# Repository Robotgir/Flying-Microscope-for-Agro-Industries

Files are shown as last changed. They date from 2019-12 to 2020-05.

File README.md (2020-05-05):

# Flying Microscope (SPECTORS)
This repo contains hardware and software details for the spore collector device which can be remotely controlled via Spectors Cockpit. Live image can be acessed on Spectors Cockpit.
## Code 
contains main script file named sporecollector1.py and its dependensies
### noteson_code.docx 
few details about the input variables in sporecollector1.py

## Docs 
contais system chart hand sketch  (Digital version yet to come)
### SystemChart.png coming soon
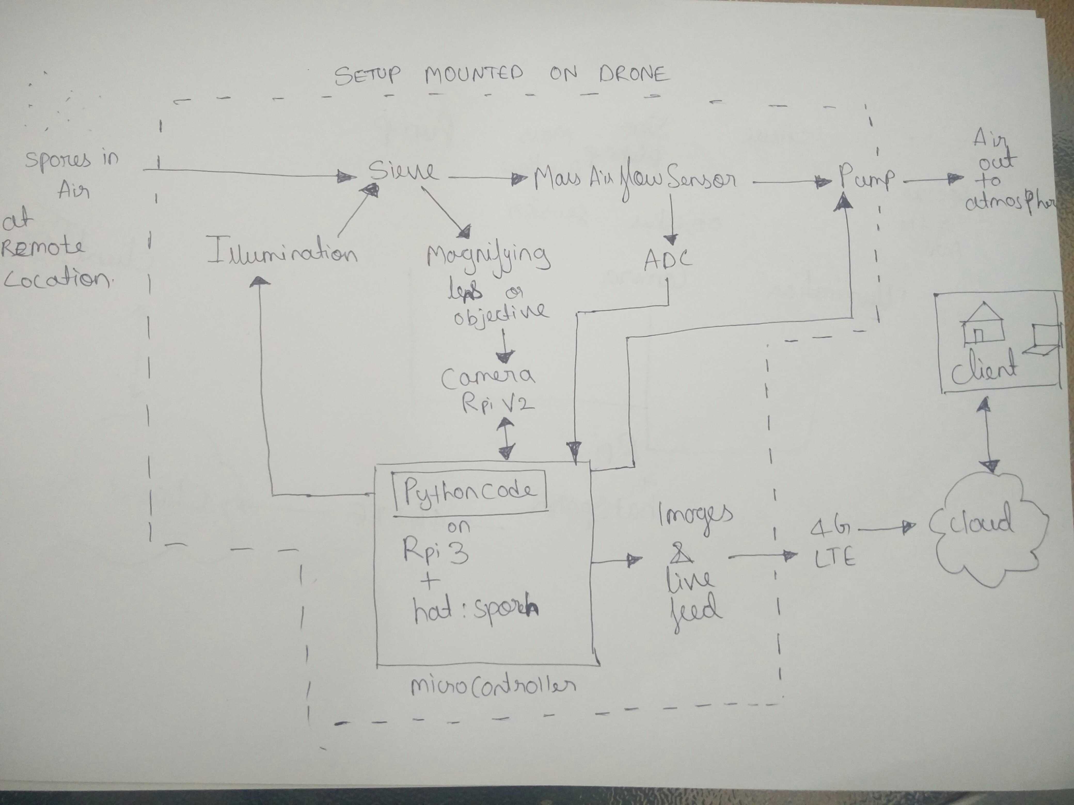
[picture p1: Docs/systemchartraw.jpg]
//

## Hardware
### camera_sieveholderassembly
contains priliminary and current designs for the spore collector device
### PCB (RPI HAT)
 contains Eagle board and schematic files for the PCB design
### productdata sheets
contain all the hardware components datasheets
#### PCB_connection_notes.docx 
contains details of how to setup the PCB AS Rpi-hat, connections with other components.

## Spore collection images
Images obtained from the measurment process
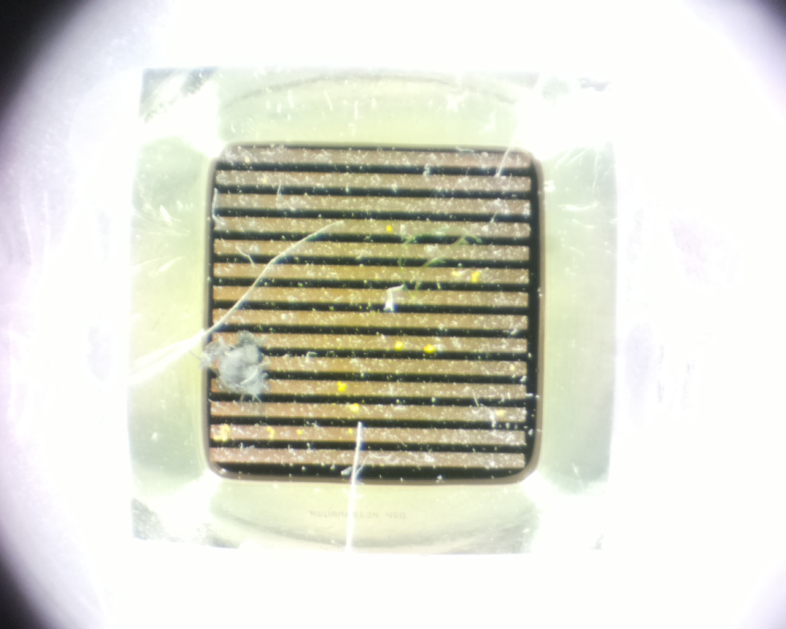
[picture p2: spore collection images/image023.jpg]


## PCB-Rpi-hat
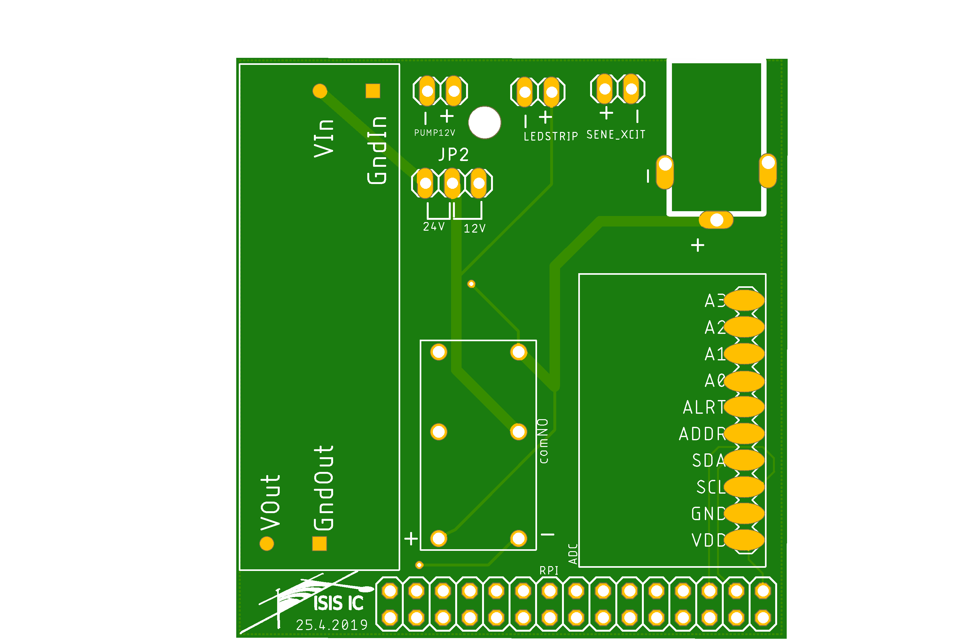
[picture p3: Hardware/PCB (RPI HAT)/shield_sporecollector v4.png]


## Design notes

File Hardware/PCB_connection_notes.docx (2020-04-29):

Two options available to choose:
The design of Rpi hat for spore collection device can be integrated with either 24V or 12V pump.
On board voltage step up regulator steps up the fixed input 12V to 24V (can be used when 24V pump is used in the spore collector device).

Steps to connect Rpi hat follow:

1. Use a jumper connector to connect the pin pair either 24V or 12V (Red circle) pair depending on the rated - pump voltage installed in the device.
2. If using a 12V pump, connect the power supply cables of pump to the 12V + - pins on the Rpi hat (blue circle).
3. If using 24V pump, connect the power supply cables of pump to the Vout and Gndout pins (yellow circle )on the Rpi-hat.
4. Power supply cables of the Led-strip to the pins in purple circle.
5. Sensor power supply cables to the respective pins as indicated on the Rpi-hat.
Note:
If the jumper pin is connected wrongly then the pump will not be supplied power as it can be seen the outlets for 12V and 24V are different.
Warning!!|


If pumps are not connected in respect to their designated pins based on their rated voltage malfunctioning of the pump and the Rpi is inevitable.

Powering the Rpi-hat:
Supply 12 V with min 3 amp

Powering the Rpi:

The Rpi, itself has to be powered separately with 5V 2.5 amp.

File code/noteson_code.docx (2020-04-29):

Location on the Rpi sd card:
cd Documents/sporecollector/Sporecollector1.py

Notes on the code, for the spore collection process:

Amount of liters to be sucked can be changed by assigning desired amount of liters to be sucked to the variable z of function measurmentprocess() in “sporecollector1.py”

Variable “i” of function ledcam() in “sporecollector1.py”sets the number of pictures to be taken during the measurement process

Interval at which the pictures are to be taken can be set by changing the j in time.sleep(j).
where, j is in seconds.

To stop the measurement process:
Hit ctrl+c

Location of the captured images:
"/home/pi/Documents/sporecollector/trailcam"

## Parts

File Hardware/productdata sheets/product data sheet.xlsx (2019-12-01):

PRODUCT | COMPANY NAME | MODEL NUMBER | SPECIFICATION | VOLTAGE [V] | CURRENT [mA] | POWER [W] | DIMENSIONS (L*W*H) [mm] | WEIGHT [g] | LINK
Pump | Thomas | G 24/07 N 50311 | 18 L/min | 24 | 1600 | 38.4 | 100*57*57 | 500 | https://www.gd-thomas.com/en/media/catalog/gdt_brochure/Miniature_Series_1853--17000115.pdf
Sensor | Honeywell | AWM 5102 VN | 0 - 10 SLPM | 10 | 10 | 0.1 | 163*32.3*35.6 | 30 | https://www.digikey.de/products/de?keywords=480-3094-ND
Micro computer | Raspberry Pi | zero W | 1 GHz, 512 MB | 5 | 160-230 | 0.8 | 65*30*5 | 10
Battery | LiPol Battery | LP3SD | 11.1 V, 4000 mAh |  |  |  | 135*41*25 | 329 | http://www.lipolbattery.com/LiPo%20battery%2011.1V%204000mAh%2025C.html
Micro sieves
Tubes and connectors
Buck circuit
Boost circuit
ADC | Adafruit | ADS 1015 | 12 Bit, 4 Channel | 2017-05-02 | 0.15 | 0.00075 |  |  | https://www.adafruit.com/products/1083

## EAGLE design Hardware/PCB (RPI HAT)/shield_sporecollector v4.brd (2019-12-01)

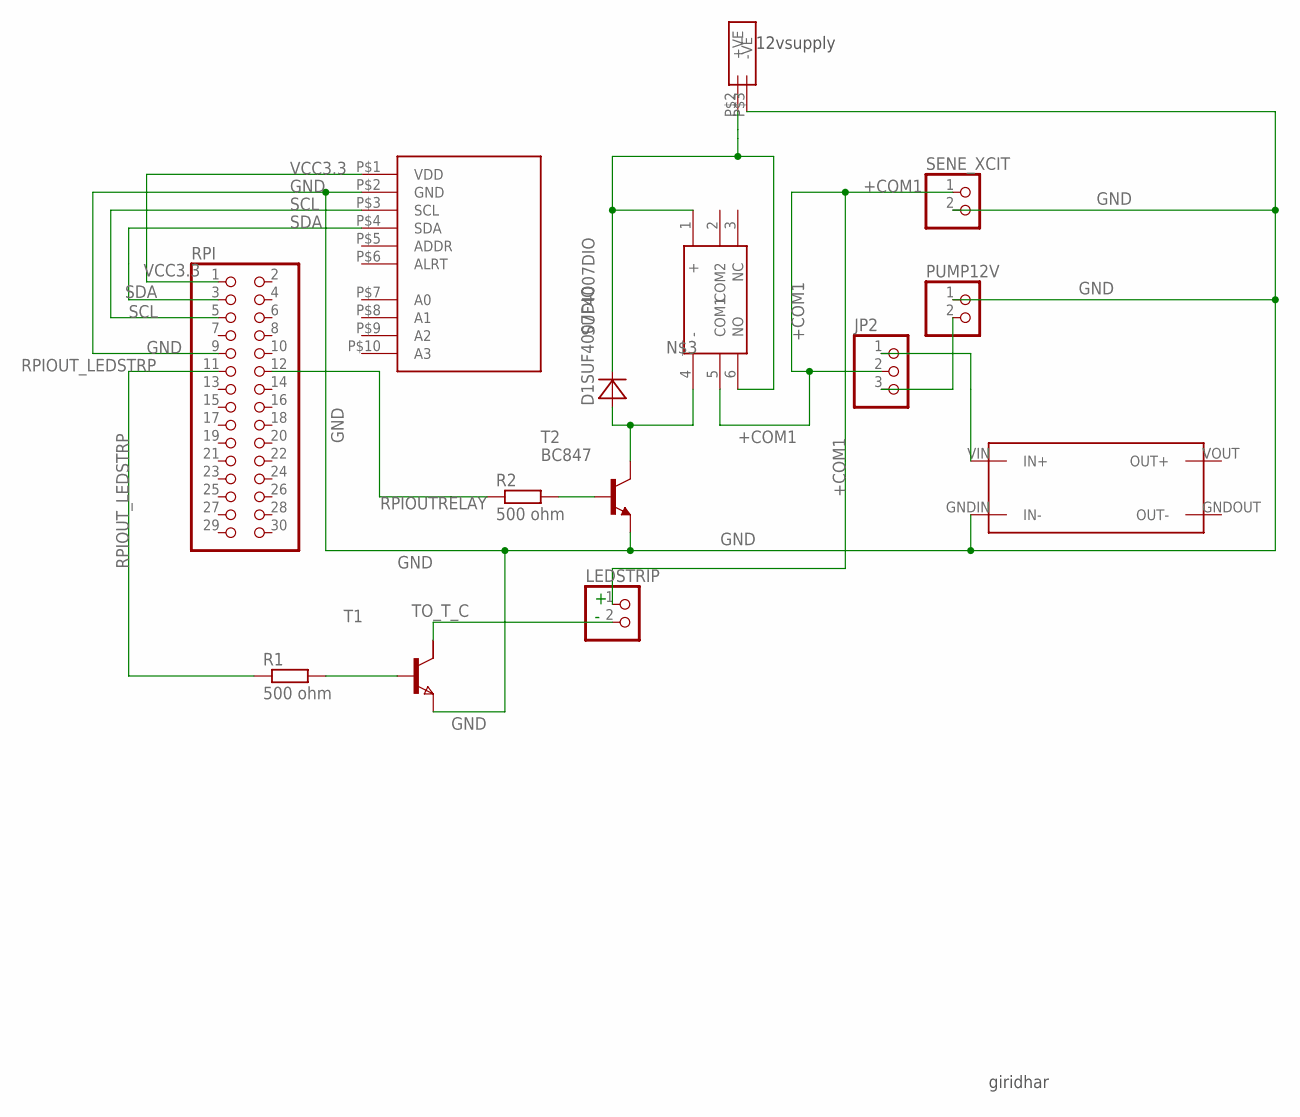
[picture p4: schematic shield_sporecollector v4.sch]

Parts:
BUCHSE12VINPUT: BUCHSE9.8X14.6
D1SUF4007DIO: SUF4007DIO; SUF4007
JP2: PINHD-1X3; 1X03
LEDSTRIP: PINHD-1X2; 1X02
PUMP12V: PINHD-1X2; 1X02
R1, R2: 500 ohm; R0603
RPI: PINHD-2X15; 2X15
SENE_XCIT: PINHD-1X2; 1X02
STEPUP12TO24V: 24VSTEPUPPOLOLUSMDSMD; STEP-UP24VSMD
T1: NPNSOT223; SOT223
T2: BC847; SOT23
U$3: ADC-4CH-ADS1115/WITHOUTHOLESADC-ADS1115WITHOUTHOL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; ADC-4CH-ADS1115/WITHOUTHOLES
U$4: G6B-2114POMRON; G6B-2114P

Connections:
+COM1: JP2.2, LEDSTRIP.1, SENE_XCIT.1, U$4.5 (COM1)
GND: BUCHSE12VINPUT.P$3 (-VE), PUMP12V.1, RPI.9, SENE_XCIT.2, STEPUP12TO24V.GNDIN (IN-), T1.3 (E), T2.2 (E), U$3.P$2 (GND)
unnamed: R2.2, T2.1 (B)
unnamed: R1.2, T1.1 (B)
unnamed: BUCHSE12VINPUT.P$2 (+VE), D1SUF4007DIO.C, U$4.1 (+), U$4.6 (NO)
unnamed: JP2.3, PUMP12V.2
unnamed: JP2.1, STEPUP12TO24V.VIN (IN+)
RELAY_T3_-_COIL: D1SUF4007DIO.A, T2.3 (C), U$4.4 (-)
RPIOUTRELAY: R2.1, RPI.12
RPIOUT_LEDSTRP: R1.1, RPI.11
SCL: RPI.5, U$3.P$3 (SCL)
SDA: RPI.3, U$3.P$4 (SDA)
TO_T_C: LEDSTRIP.2, T1.2 (C1)
VCC3.3: RPI.1, U$3.P$1 (VDD)

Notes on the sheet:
giridhar
12vsupply

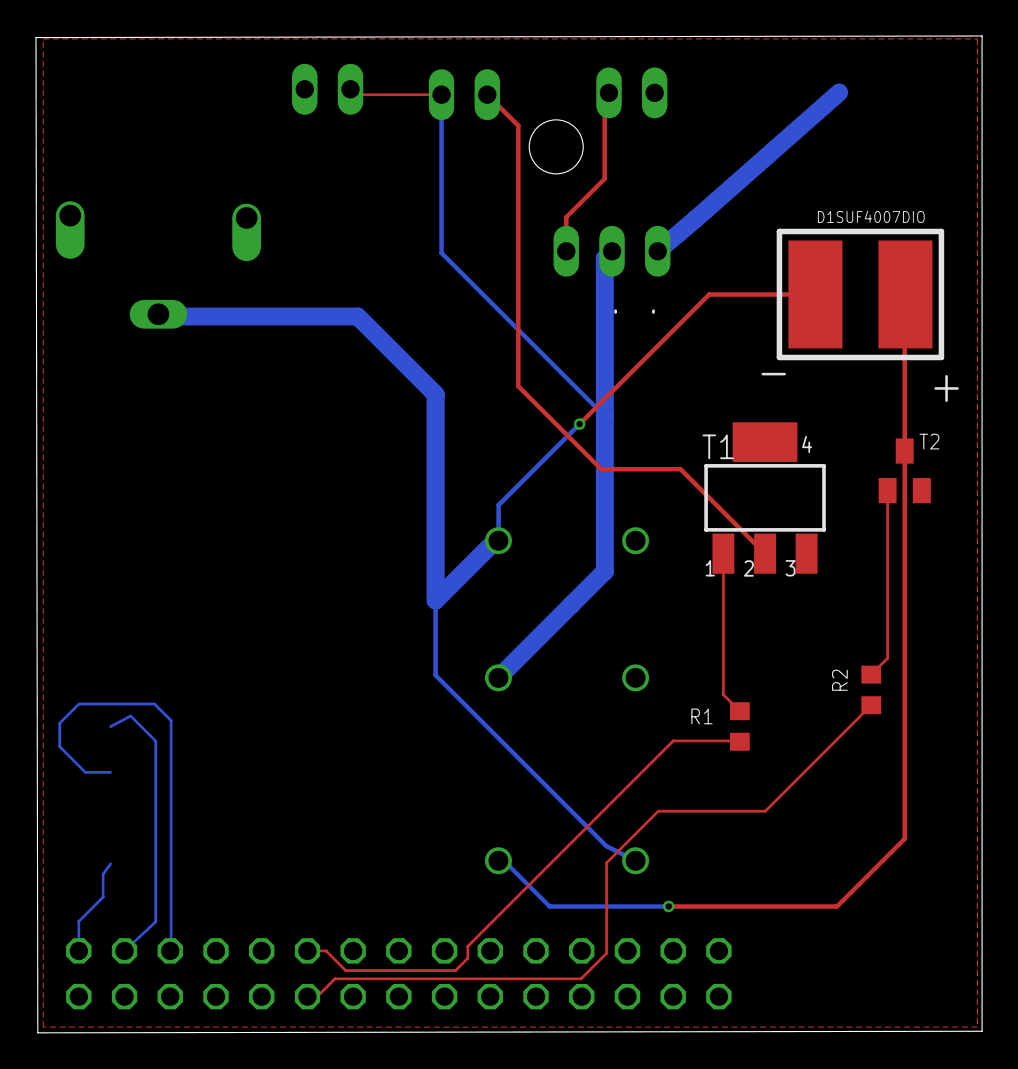
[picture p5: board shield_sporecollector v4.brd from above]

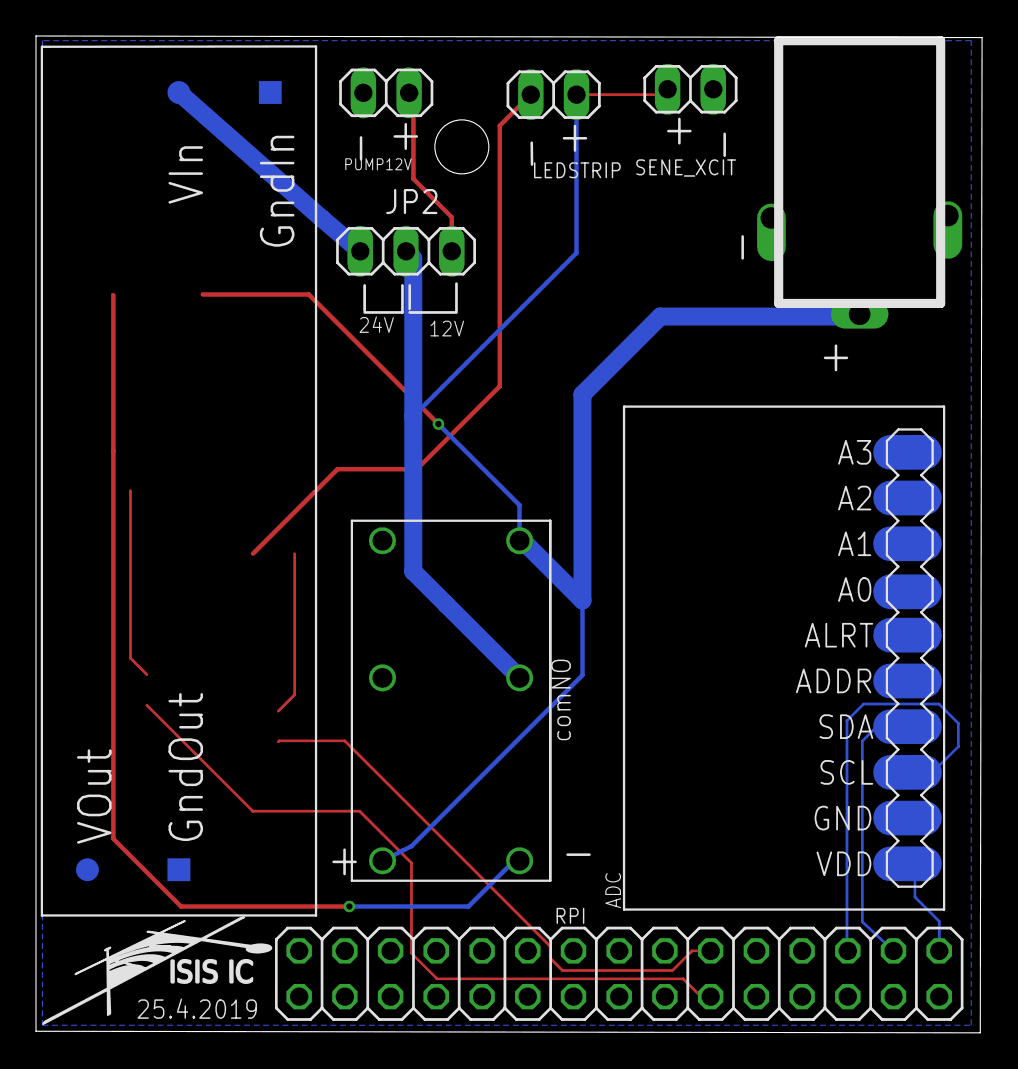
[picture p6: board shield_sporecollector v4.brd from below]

Board: 2 copper layers, 52.6 x 55.4 mm, 14 parts (9 on the bottom side), 14 nets.

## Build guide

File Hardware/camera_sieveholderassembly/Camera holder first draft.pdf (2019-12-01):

Camera holder first draft

Objective: The apparatus is designed to serve two main functions, the first function is to hold the micro pi camera as an attachment for the spore collector device and the second function is to maintain clear and sharp view of the sieve using two vertical focusing power screw sets.

Design visualization:

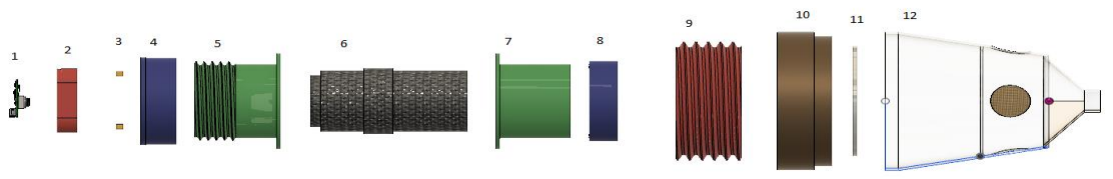
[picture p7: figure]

Figure 1 Camera holder exploded view.

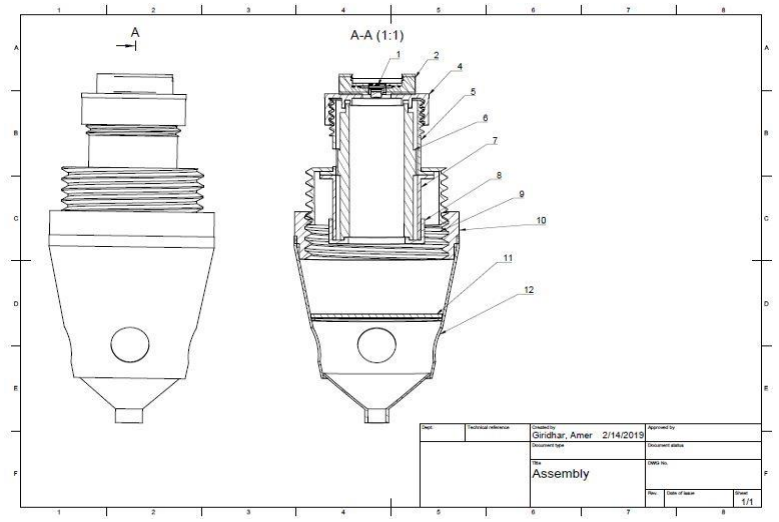
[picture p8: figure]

Figure 2 Camera holder assembly drawing.

List of components:

Part
Number
| Part Name | Function and description

### 1 Pi Camera V2

| module | A micro HD pi camera module with 8 mp is installed for capturing high resolution
| | pictures of the sieve.
2 | Camera base | Camera Holder for maintaining position and protection against hazards and short
| | circuits. It also allows axial rotation of the pi camera for vertical alignment with the
| | sieve.
3 | Keys | Connection between the camera holder and the objective cap.
4 | Cap | Bottom tightening

### 5 Objective

| compartment 1 | Bottom centering part of the objective.
6 | Objective (Lens) | 130X objective with fine focal length adjustment.

### 7 Objective

| compartment 2 | Upper centering part of the objective.
8 | Cap | Alignment part.

### 9 Rough focusing

| adjustment thread | Used for upper tightening and rough focusing with a pitch of 6 mm.

### 10 Working distance

| adjuster. | Used for adjusting the effective working distance for monitoring the sieve.
11 | Optical glass layer | Thin sheet of optical glass serves as a transparent separator between the optical set
| | and the air flow environment in the suction chamber created by the air pump.
12 | Suction chamber | Works as the sieve holder and allowing air tight flow 4 inlet holes on the chamber
| | surface filtered by meshes.

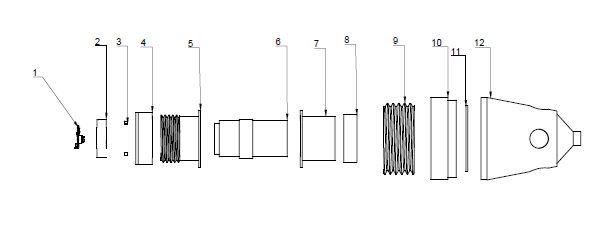
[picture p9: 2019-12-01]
Hardware/camera_sieveholderassembly/Exploded view.JPG

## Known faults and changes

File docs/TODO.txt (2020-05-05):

hand sketch uploaded
hand sketch to digital version by trainee

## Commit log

2019-12-01 first update
    [T960setupw5008.xlsx, product data sheet.xlsx, shield_sporecollector v4.brd, shield_sporecollector v4.sch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]
2020-04-29 organized content
    readme update
    [product data sheet.xlsx, shield_sporecollector v4.brd, shield_sporecollector v4.sch]
2020-04-29 edit readme
    [shield_sporecollector v4.brd, shield_sporecollector v4.sch]

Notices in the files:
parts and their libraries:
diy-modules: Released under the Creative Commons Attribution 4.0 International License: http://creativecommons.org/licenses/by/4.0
